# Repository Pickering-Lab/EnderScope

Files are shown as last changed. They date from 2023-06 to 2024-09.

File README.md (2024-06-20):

# EnderScope
The EnderScope is a low-cost scanning microscope, based on the mechanics of the ubiquitous 3D printer, the **Ender 3 Pro**. The hotend of the printer is replaced with an optics module, allowing for the reliable and well calibrated motion system of the 3D printer to be used for automated scanning over a large area.

## Citing
**EnderScope: a low-cost 3D printer-based scanning microscope for microplastic detection**
Niamh Burke, Gesine Müller, Vittorio Saggiomo, Amy Ruth Hassett, Jérôme Mutterer, Patrick Ó Súilleabháin, Daniel Zakharov, Donal Healy, Emmanuel G Reynaud, Mark Pickering
Philosophical Transactions A, 2024, 382 (2274) 20230214, http://doi.org/10.1098/rsta.2023.0214

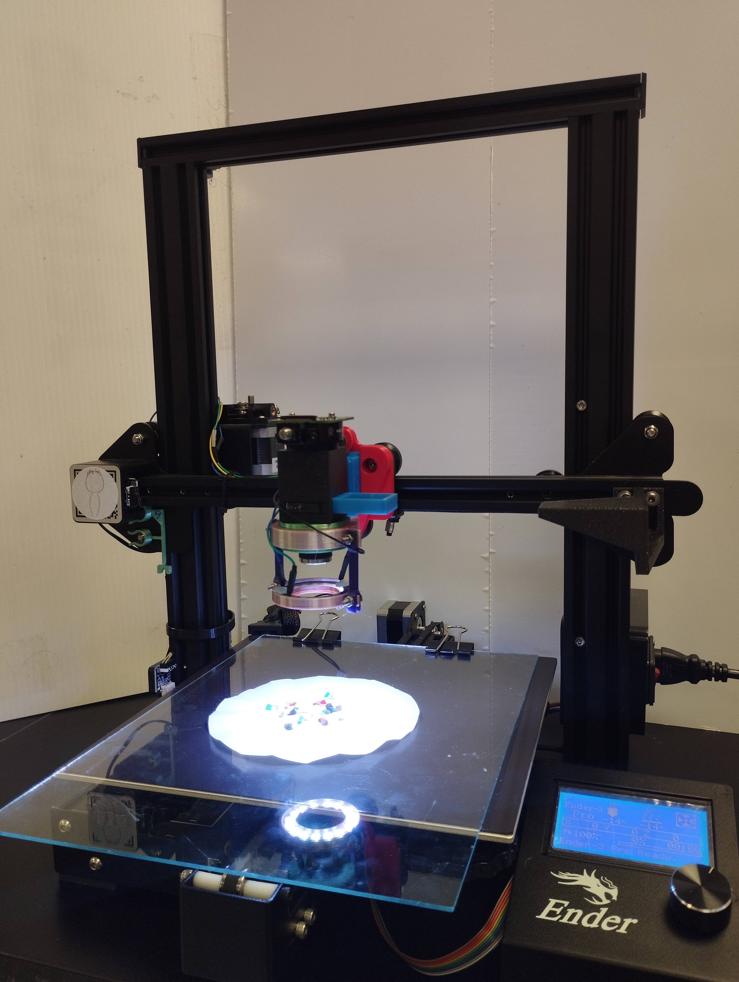
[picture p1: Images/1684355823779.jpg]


## We have reached our funding target on Experiment.com! 🎉
Thanks to your support we have reached our funding target on Experiment.com. Our next step is to get the EnderScope in the hands of Maker Spaces, Community Groups and Libraries accross Ireland. 

Interested in taking part? Contact us on Twitter [@PickeringLab](https://x.com/PickeringLab?s=20) or [@Niamh_deBurca](https://twitter.com/Niamh_deBurca). Watch this space 👀!



# How to Build Your Own EnderScope!
## Hardware
### Bill of Materials
| Part | Qty | Purpose | Source | Price € |
| ----------- | ----------- | ----------- | ----------- | ----------- |
| **Non-printed Parts** |
| Ender 3 Pro | 1 | Motion system of EnderScope | [Link to Ender](https://ie.farnell.com/creality-3d/ender-3-pro/3d-printer-220-x-220-x-250mm-1/dp/2945489) | 224.65 |
| Keyboard & Mouse | 1 | Control of EnderScope | [Link to keyboard and mouse](https://www.amazon.co.uk/Richer-R-Keyboard-Portable-Lightweight-Ultra-Thin-Black/dp/B07CRM63WW/ref=sr_1_5?crid=23O5WNS7BQETO&keywords=usb+keyboard+and+mouse+small&qid=1687527843&sprefix=usb+keyboard+and+mousesmall%2Caps%2C48&sr=8-5) | 15.48 |
| Monitor | 1 | Display for EnderScope | [Link to Monitor](https://www.amazon.co.uk/Dell-Professional-Widescreen-Backlit-Monitor/dp/B00F6390EI/ref=sr_1_5?crid=155O3H11AT8RS&keywords=flat+panel+monitor&qid=1687528400&sprefix=flat+panel+monitor%2Caps%2C56&sr=8-5) | 58.16 |
| HDMI-micro HDMI | 1 | To connect Raspberry Pi to Monitor | [Link to HDMI-microHDMI](https://ie.farnell.com/raspberry-pi/t7733ax/cable-micro-hdmi-hdmi-plug-2m/dp/3107129?gclid=CjwKCAjwhdWkBhBZEiwA1ibLmHy8lcH_6-mT7bqlnekisB4aghKRtLZO5OpQ6GcXcyXmCx-YCe7CPRoCSIsQAvD_BwE&gross_price=true&CMP=KNC-GIE-GEN-SHOPPING-PerformanceMax-TEST-962) | 5.62 |
| 4x RMS Finite Conjugate Objective Lens | 1 |  | [Link to objective lens](https://www.amazon.com/Compound-Microscope-Achromatic-Objectives-Conjugate/dp/B08HW6XMQQ/ref=sr_1_2?crid=2XI5O2ZMWLERR&keywords=rms+finite+conjugate+objective+lens&qid=1674738740&sprefix=rms+finite+conjugate+objective+lens%2Caps%2C127&sr=8-2) | 8.63 |
| Raspberry Pi HQ Camera | 1 | | [Link to HQ Camera](https://ie.farnell.com/raspberry-pi/rpi-hq-camera/rpi-high-quality-camera-12-3-mp/dp/3381605?gclid=CjwKCAjwhdWkBhBZEiwA1ibLmLPRsZ-kTz68qI1Buou0t5rqj3jjkPpFDO3mcRCRjVkKVoDt2jtdiRoC4SUQAvD_BwE&gross_price=true&CMP=KNC-GIE-GEN-SHOPPING-PerformanceMax-No-Impressions) | 56.54 |
| Raspberry Pi 4 Model B | 1 | A low-cost computer used to run the EnderScope | [Link to Raspberry Pi](https://ie.farnell.com/raspberry-pi/rpi4-modbp-4gb/raspberry-pi-4-model-b-4gb/dp/3051887) | 62.20 |
| Pi camera CSI cable (Long ~100cm) | 1 | Connect Raspberry Pi to HQ Camera | [Link to CSI Cable](https://ie.farnell.com/mcm/83-17610/csi-dsi-extension-cable-1-meter/dp/2801336?st=100cm%20csi%20cable) | 6.32 |
| 5V Power Supply USB Type C | 2 | To power Raspberry Pi | [Link to Raspberry Pi power supply](https://ie.rs-online.com/web/p/raspberry-pi-power-supplies/1873424?cm_mmc=IE-PLA-DS3A-_-google-_-CSS_IE_EN_Pmax_Test-_--_-&matchtype=&&s_kwcid=AL!14853!3!!!!x!!&gclid=Cj0KCQjw7uSkBhDGARIsAMCZNJvJgLZ8F8H9JMSdhJQLBEwR4ra1u99iysdaG6aJ2BMPwZ8ZWJeXU8waAowZEALw_wcB&gclsrc=aw.ds) | 9.69 |
| 5V Power Supply USB | 2 | To power Arduino Nano| [Link to 5V power supply](https://www.amazon.co.uk/Charger-Adaptor-Compact-Charging-Samsung/dp/B0BV65Y6B2/ref=sr_1_9?crid=2RVFZQS96QDYE&keywords=5v+wall+charger&qid=1687785970&sprefix=5v+wall+%2Caps%2C58&sr=8-9) | 5.98 |
| Arduino Nano | 1 | To control LED ring | [Link to Arduino](https://store.arduino.cc/products/arduino-nano?queryID=undefined) | 21.60 |
| Push Button | 1 | Turn LED ring on, green or white | [Link to push buttons](https://www.amazon.co.uk/Gikfun-6x6x5mm-Switch-Arduino-EK1019U/dp/B07DQL2GG4/ref=sr_1_1_sspa?crid=17EAN9SJTHE6H&keywords=arduino+push+button&qid=1687538997&sprefix=arduino+push+button%2Caps%2C59&sr=8-1-spons&sp_csd=d2lkZ2V0TmFtZT1zcF9hdGY&psc=1) | 8.09 |
| 220 Ohm Resistor | 1 | For push button | [Link to resistors](https://www.amazon.co.uk/Projects-50EP114220R-220-Resistors-Pack/dp/B0BQ1W9RHK/ref=sr_1_4_sspa?crid=3U55YJR7HT7W&keywords=220+ohm+resistor&qid=1687539054&sprefix=220%2Caps%2C58&sr=8-4-spons&sp_csd=d2lkZ2V0TmFtZT1zcF9hdGY&psc=1) | 6.08 |
| 170 pin breadboard | 1 | For arduino and push button | [Link to breadboard](https://www.amazon.co.uk/SIGNAL-PSG-BB-170W-2BP-Breadboard-Plastic-34-5mm/dp/B01IO3IS12/ref=sr_1_3?crid=2BN9MA6U1KGBD&keywords=170+pin+breadboard&qid=1687539158&sprefix=170+pin+breadboard%2Caps%2C46&sr=8-3) | 3.85 |
| Male to Male Jumper Wires | 7 | For wiring of LED ring and push button | [Link to jumper wires](https://www.amazon.co.uk/2-54mm-Jumper-Wires-Cables-female/dp/B09T3QF6VP/ref=sr_1_48?adgrpid=63845174572&hvadid=291338039024&hvdev=c&hvlocphy=1007850&hvnetw=g&hvqmt=e&hvrand=17576542995084926756&hvtargid=kwd-300565221968&hydadcr=18912_1787284&keywords=male%2Bto%2Bmale%2Bjumper%2Bwires&qid=1687783718&sr=8-48&th=1) | 1.99 |
| USB type A - mini B Cable | 1 | To connect Arduino Nano to 5V power supply | [Link to USB mini cable](https://www.amazon.co.uk/LINDY-36722-Mini-B-Cable-Anthra/dp/B07FN1W4JL/ref=sr_1_3?keywords=mini%2Busb%2Bcable&qid=1687784057&sr=8-3&th=1) | 3.05 |
| USB type A - Micro USB Cable | 1 | To connect Ender to Raspberry Pi| [Link to micro USB cable](https://www.amazon.co.uk/AmazonBasics-Male-Micro-Cable-Black/dp/B07232M876/ref=sr_1_1_ffob_sspa?crid=276BWYDT9STTD&keywords=micro%2Busb%2Bcable&qid=1687784254&s=computers&sprefix=micro%2Busb%2B%2Ccomputers%2C55&sr=1-1-spons&sp_csd=d2lkZ2V0TmFtZT1zcF9hdGY&th=1) | 5.07 |
| Lighting Gels | 1 | Used as Emmission Filter | [Link to lighting gels](https://www.aliexpress.com/item/32695436168.html?pdp_npi=2%40dis%21EUR%21%E2%82%AC%208%2C78%21%E2%82%AC%208%2C78%21%21%21%21%21%4021032fa616703165944567885e866e%2165363130207%21btf&_t=pvid:451ae040-dcc0-4a03-897e-5453e0968200&afTraceInfo=32695436168__pc__pcBridgePPC__xxxxxx__1670316594&spm=a2g0o.ppclist.product.mainProduct) | 7.66 |
| 16 LED Ring | 1 | Illumination Source for Microscope | [Link to LED ring](https://www.amazon.co.uk/Hobby-Components-Ltd-45MM-WS2812B/dp/B01I1D6O48/ref=sr_1_4?keywords=neopixel+16+led+ring&qid=1687539564&sr=8-4) | 9.53 |
| Glass from picture frame, 2mm in thickness, 21x30cm | 1 | Used as a "coverslip" | [Link to picture frame](https://www.ikea.com/ie/en/p/yllevad-frame-black-30429774/?utm_source=google&utm_medium=surfaces&utm_campaign=shopping_feed&utm_content=free_google_shopping_clicks_Decoration&gclid=Cj0KCQjw7uSkBhDGARIsAMCZNJuPV9QcnTO9ueFVAxaAVzIDQurpOPyJlUqf1WcASSWj0xErUw77xK0aAkzMEALw_wcB&gclsrc=aw.ds) | 2.00 |
| Binder Clips | 4 | To hold glass on print bed | [Link to binder clips](https://www.amazon.co.uk/Office-Files-Documents-Metal-Binder/dp/B00W0K3ENS/ref=sr_1_7?keywords=binder+clips&qid=1687796157&sr=8-7) | 2.38 |
| **Screws, Nuts and Tools** |
| M6 12mm Screw | 1 |  |  |  |
| M6 Square Nut | 1 |  |  |  |
| Alan Keys | 1 |  |  |  |
| M3 Screws and Nuts | 4 screws, 4 nuts |  |  |  |
| Scissors | 1 |  |  |  |
| **Total** |  |  |  |  |

### Printed Parts
All 3D-printable files can be found [here](Stls). All files were printed in PLA, with 0.2mm layer height, no supports needed.

## Software
All software for the EnderScope can be found [here](Software).

## Assembly Instructions
Assembly Instructions for the EnderScope can be found [here](AssemblyInstructions).

# Licence and Collaboration

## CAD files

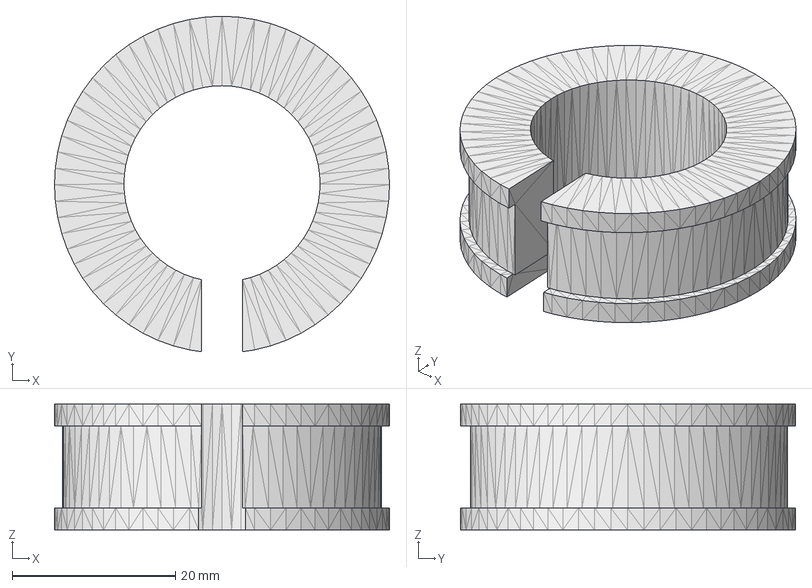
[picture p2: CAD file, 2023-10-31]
STEP/NeopixelClamp_OlympusInsert.step
41.0 x 41.1 x 15.4 mm

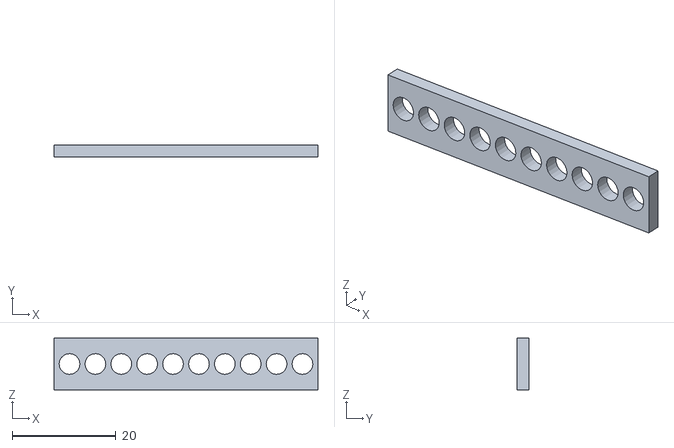
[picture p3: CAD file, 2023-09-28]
Stls/Adjustable LED option/AdjustableArm.stl
51.0 x 2.30 x 10.0

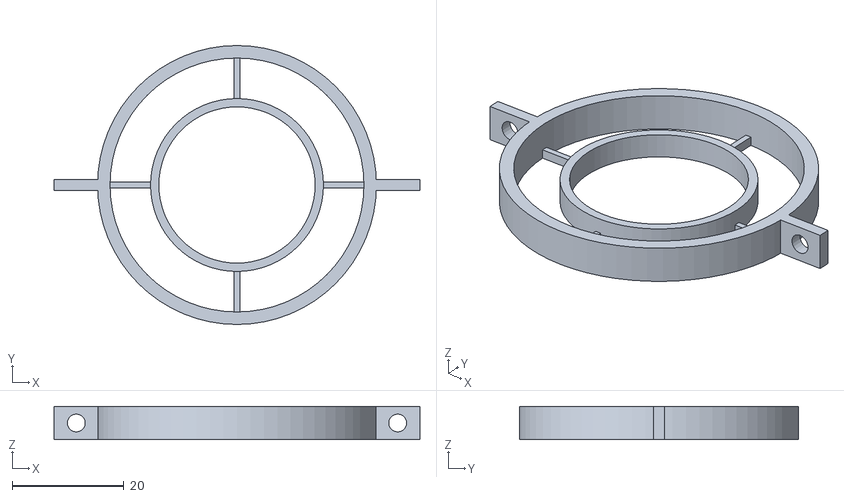
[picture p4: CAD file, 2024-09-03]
Stls/NeopixelMount.stl
65.6 x 50.0 x 6.00

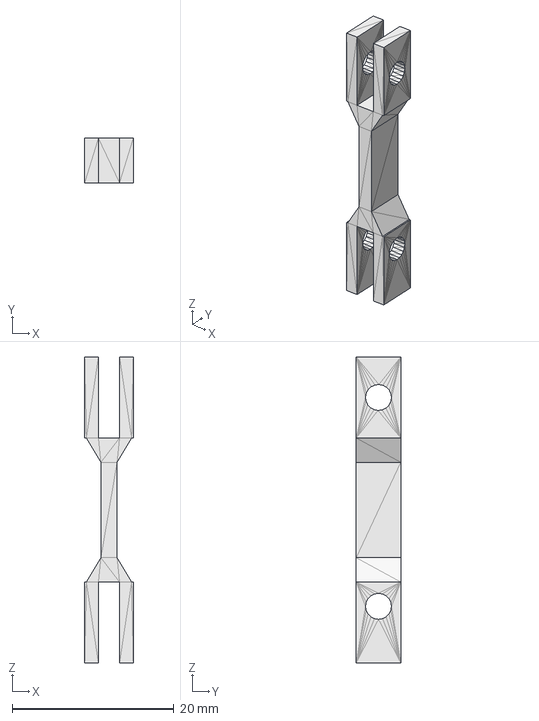
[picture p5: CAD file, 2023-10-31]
STEP/NeopixelConnecter.step
6.00 x 5.50 x 37.8 mm

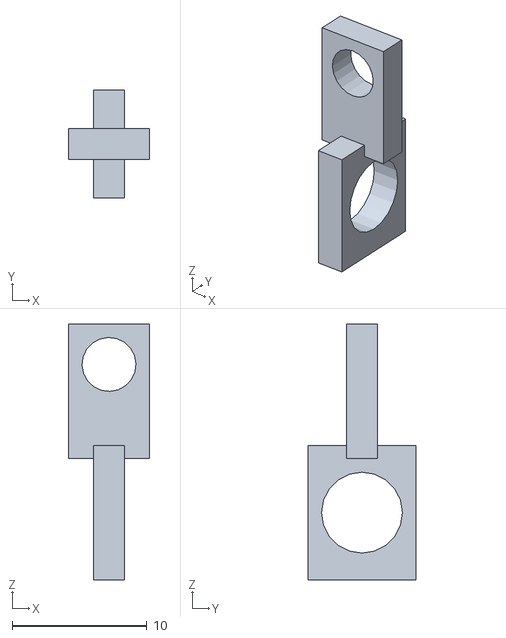
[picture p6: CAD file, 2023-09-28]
Stls/Adjustable LED option/LEDholder.stl
6.00 x 8.00 x 19.0

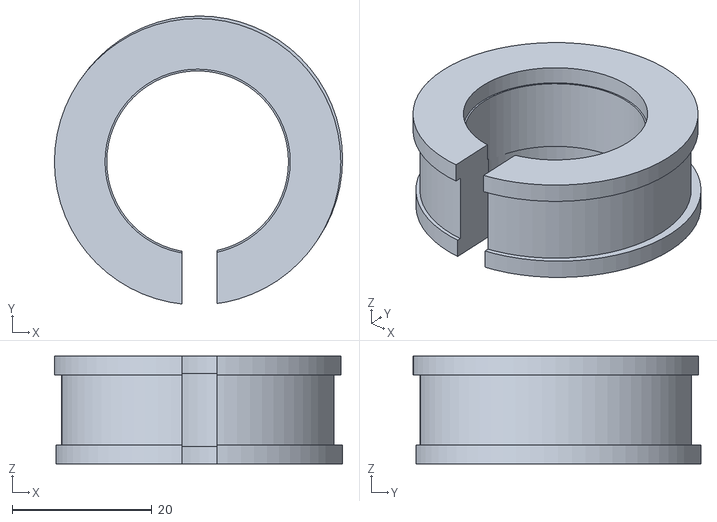
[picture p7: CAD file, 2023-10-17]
Stls/NeopixelClamp_NikonInsert.stl
41.2 x 41.2 x 15.4

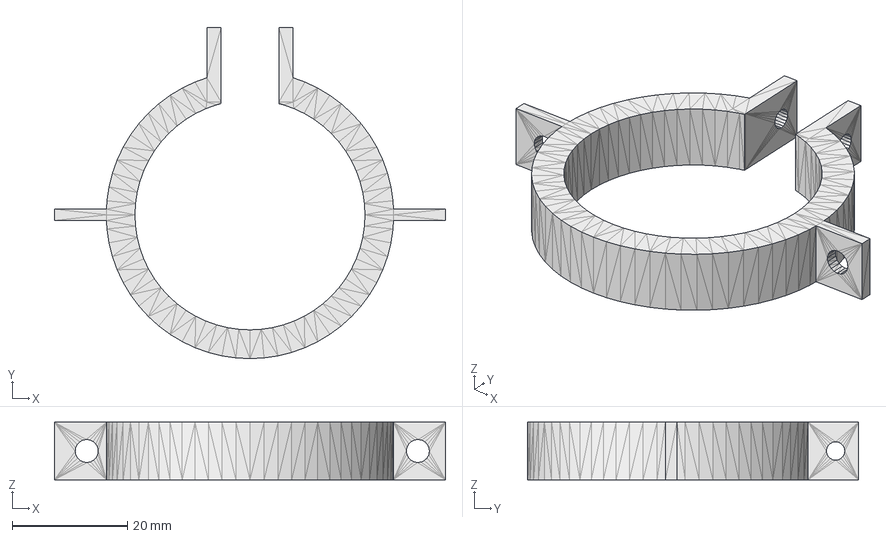
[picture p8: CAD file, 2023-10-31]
STEP/NeopixelClamp.step
68.0 x 57.6 x 10.0 mm

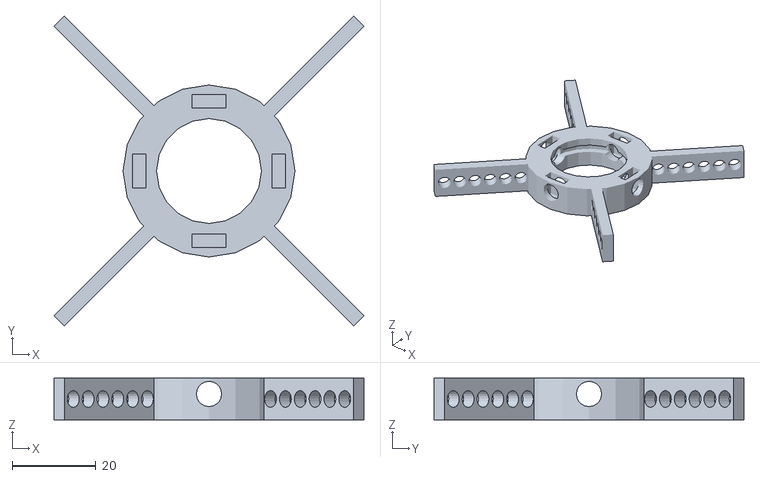
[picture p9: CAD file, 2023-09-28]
Stls/Adjustable LED option/ObjectiveClamp_Oring.stl
73.9 x 73.9 x 10.0

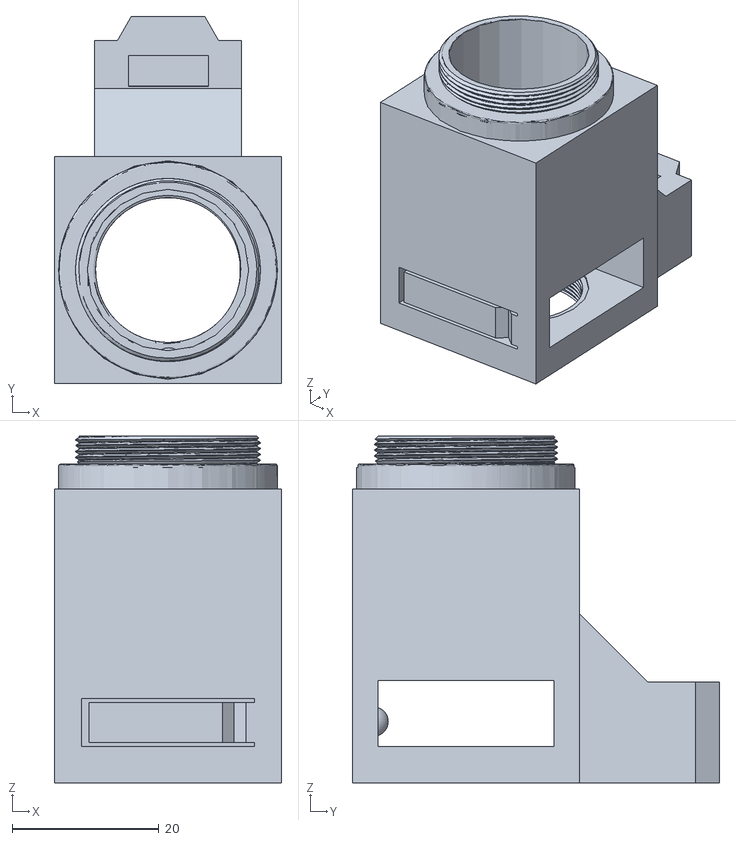
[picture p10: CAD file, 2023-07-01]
Stls/LensTube.stl
31.0 x 50.1 x 47.3

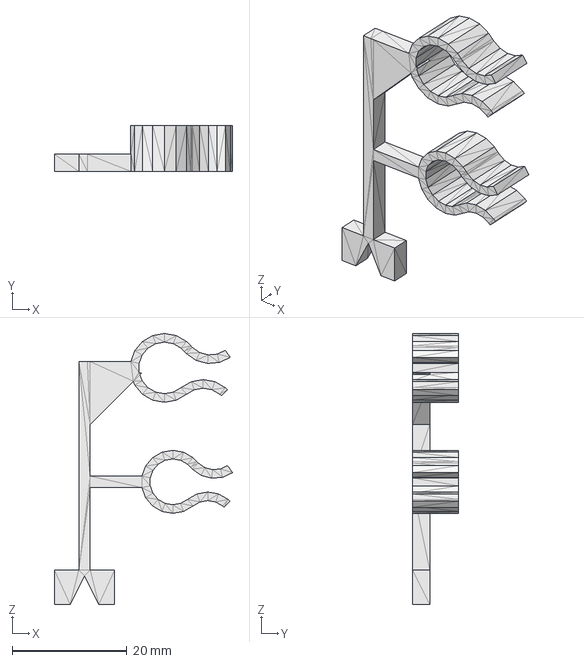
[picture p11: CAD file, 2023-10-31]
STEP/LimitSwitchExtender.step
31.1 x 8.00 x 47.3 mm

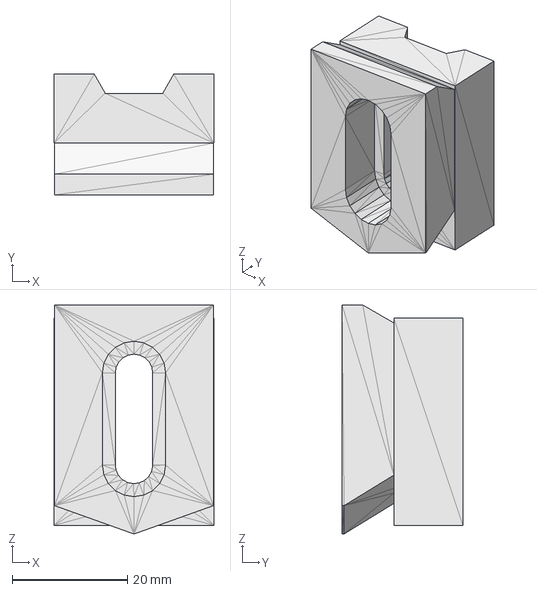
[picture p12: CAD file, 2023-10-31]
STEP/EnderScopeToolHolder.step
27.8 x 21.0 x 39.8 mm

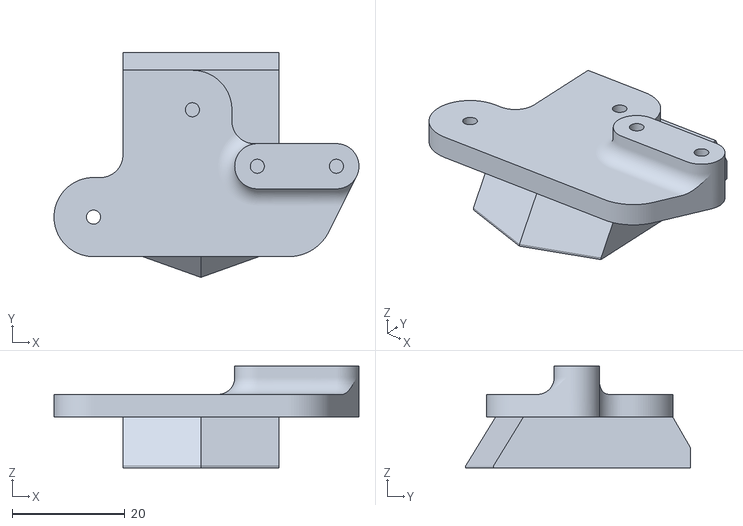
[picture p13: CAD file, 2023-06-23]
Stls/EnderHotendToolHolder.stl
54.0 x 39.8 x 18.0

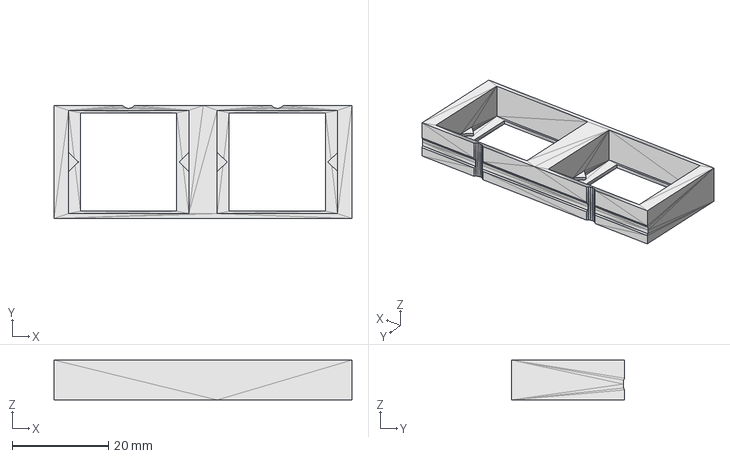
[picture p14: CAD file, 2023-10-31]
STEP/FilterSlider.step
62.0 x 23.5 x 8.30 mm

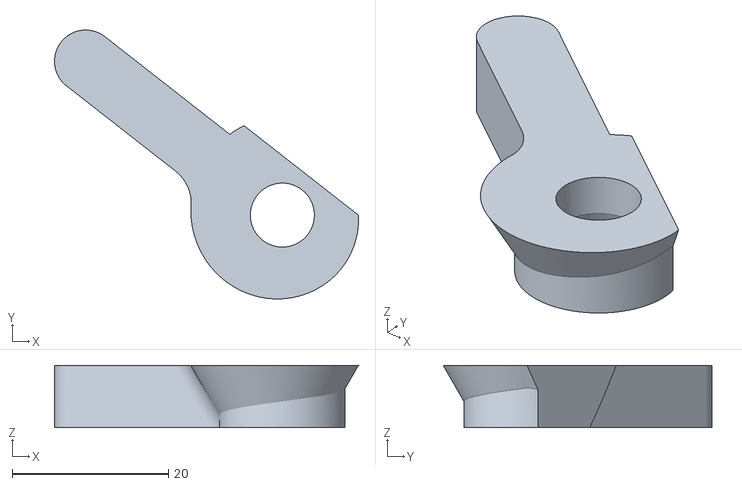
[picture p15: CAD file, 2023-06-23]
Stls/Lever.stl
39.0 x 34.5 x 8.00

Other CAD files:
Stls/NeopixelClamp_GenericInsert.stl
STEP/CableTidy.step
Stls/ToolHolderBase.stl
STEP/ArduinoNanoHolder.step
Stls/ArduinoNanoHolder.stl
Stls/CableTidy.stl
Stls/EnderScopeToolHolder.stl
Stls/FilterSlider.stl
Stls/LimitSwitchExtender.stl
Stls/NeopixelClamp.stl
Stls/NeopixelClamp_OlympusInsert.stl
Stls/NeopixelConnecter.stl

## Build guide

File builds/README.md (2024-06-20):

# A page to gather EnderScope builds and variants
| Printer | Camera | Lens | Illumination | Software | Builder | Application | Comments |
| ----------- | ----------- | ----------- | ----------- | ----------- | ----------- | ----------- | ----------- |
| Ender 3  | Raspberry Pi HQ | 4x | Neopixels with Arduino Nano button | Scripts (link)| Niamh Burke| Detecting microplastics |Original EnderScope |
| Ender 3 S1 | Raspberry Pi HQ | 10x | Neopixels over RPi GPIO | Scripts (meander scan) (link)| Hugo LeGuenno & Jerome Mutterer| Cyanobacteria |Built for MiFoBio2023 |
| Ender 2 Pro | Raspberry Pi Cam V2.1 | - | Neopixels with Arduino Uno firmware for software control (link)| GUI with stage and illumination control and multiposition time-lapse (link)| Jerome Mutterer & Hugo LeGuenno | Seed growth in multiwell plates |Built for MiFoBio2023 |
|- |- |- | Simple Colimation Usson Device (link) |-|Hugo LeGuenno & Yves Usson|Fluorescence| Single high-power RGB LED with easy colimation| 
| - | - | - | Enderlights | [Arduino firmware](enderlights/enderlights.ino)| Jerome Mutterer| Neopixels illumination device that can be driven with a custom set of serial commands |- |

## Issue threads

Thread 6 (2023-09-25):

### ISSUE TITLE
Are there any suggested alternatives for the LED ring / specifications for lighting gels?

### ISSUE THREAD

**Issue by rooksoup** [Pickering-Lab/EnderScope#6]
Hiya,

We have most of the parts to build an EnderScope ourselves and are just missing the cover glass, LED ring and lighting gels. It appears that the LED ring you list is only available through Amazon or that supplier and the lighting gels via AliExpress - are there any suggested equivalents for these that might be more accessible through the annoying constraints of university wholesale suppliers? Has anyone had success with anything a bit different (I imagine it might require some trial and error without the provided Arduino sketch)?

If you have any kind of specs for the LED ring etc. I can have a go at finding something similar and report back :)

**Comment by niamh-deburca** [comment]
Hey,

So for the LED ring, the one we have listed is a cheaper version of the [Adafruit NeoPixel 16 LED ring](https://www.adafruit.com/product/1463). You could swap this out for any LEDs but if you want something that fits in the LED holder it needs to have the following dimensions: 

![image](https://github.com/Pickering-Lab/EnderScope/assets/130670399/b792aff2-63b5-4bb3-94c8-4665c599cea1)

We have also designed an adjustable LED holder. This allows you to hold individual 5mm 2-pin LEDs on adjustable arms and position them around the objective lens. It's a little fiddly to use which is why I didn't have it up on the repository until now but it should be there for you now in case you have some 2-pin LEDs lying around and want to try it.

For the lighting gels we have also tried these [Roscolux filters](https://www.edmundoptics.eu/f/roscolux-color-filter-swatchbook/12186/) which can be bought from Edmund Optics. They work just as well, not expensive and you can get a big swatch book where each filter comes with its own spectral chart. When we are looking to see Nile Red fluorescence, we have found that the Rose pink #342 filter from the swatch book works really well (when you double up two layers of the filter it works especially well).

Hope this helps! Looking forward to seeing another EnderScope in the wild :)

**Comment by rooksoup** [comment]
That's fantastic to know, thank you! Will hopefully report back soon once we get everything together and have a go.

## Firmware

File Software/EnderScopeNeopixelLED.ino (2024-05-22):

#include <Adafruit_NeoPixel.h>

#define PIN            6  // Define the pin to which your NeoPixel strip is connected
#define NUM_LEDS       16 // Define the number of NeoPixels in your strip
#define BUTTON_PIN     2  // Define the pin where the push button is connected

Adafruit_NeoPixel strip = Adafruit_NeoPixel(NUM_LEDS, PIN, NEO_GRB + NEO_KHZ800);

int buttonState = HIGH;
int lastButtonState = HIGH;
unsigned long lastDebounceTime = 0;
unsigned long debounceDelay = 50;
bool ledOn = false;

void setup() {
  strip.begin();
  strip.show(); // Initialize all pixels to 'off'
  pinMode(BUTTON_PIN, INPUT_PULLUP);
}

void loop() {
  int reading = digitalRead(BUTTON_PIN);
  if (reading != lastButtonState) {
    lastDebounceTime = millis();
  }

  if ((millis() - lastDebounceTime) > debounceDelay) {
    if (reading != buttonState) {
      buttonState = reading;

      if (buttonState == LOW) {
        // Button was pressed
        if (ledOn) {
          turnWhite(); // Turn NeoPixels white
          ledOn = false;
        } else {
          turnGreen(); // Turn NeoPixels green
          ledOn = true;
        }
      }
    }
  }

  lastButtonState = reading;
}

void turnGreen() {
  for (int i = 0; i < NUM_LEDS; i++) {
    strip.setPixelColor(i, 0, 255, 0); // Green color
  }
  strip.show();
}

void turnWhite() {
  for (int i = 0; i < NUM_LEDS; i++) {
    strip.setPixelColor(i, 255, 255, 255); // White color
  }
  strip.show();
}

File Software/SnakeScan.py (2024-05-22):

import matplotlib.pyplot as plt
import numpy as np
import serial
from picamera import PiCamera
import time


if __name__ == "__main__":
    folder = "/home/pi/" #Replace this with folder you would like your images saved in
    #Opens serial port
    ser = serial.Serial('/dev/ttyUSB0', baudrate=115200)
    xBase = "G1X"
    yBase = "Y"
    endTerm = "\n"
    speed = 18000   #max_speed
##     Uncoment to home printer at beginning of script - ***WARNING*** You must make sure objective lens will not crash in to bed before homing. Attach limit switch extender or remove optics module during homing.
#     home = "G28" + "F" + str(speed) + "\n"
#     home = home.encode('utf-8')
#     ser.write(home)
    x_mid = 0
    y_mid = 0
    startPos = xBase + str(x_mid) + yBase + str(y_mid) + "F" + str(speed) + endTerm
    startPos = startPos.encode('utf-8')
    ser.write(startPos) # go to half max
    # open camera (image acquisition)
    camera = PiCamera()

def snake(x_win, y_win, x_step, y_step):
    a = []  # List of X positions
    b = []  # List of Y positions
    x = 0
    y = 0  # Start point at the bottom left corner
    
    for j in range (y_win - 1):
    
        if j == 0 :
            
            for i in range(x_win): #increment x step
                
                if i % x_win != 0:
                    dx = x_step
                    dy = 0
                    
                elif i % x_win == 0:
                    dx = 0
                    dy = 0
                    
                x = x + dx
                y = y + dy
                
                a.append(x) #take list a and stick x into it, so 0 is first number in list
                b.append(y) #take list b and stick y into it, so 0 is first number in list 
            
        
        if j % 2 != 0:
            
            for i in range(x_win):
                
                if i % x_win != 0:
                    dx = x_step
                    dy = 0
                    
                elif i % x_win == 0:
                    dx = 0
                    dy = y_step
                    
                x = x + dx
                y = y + dy
                
                a.append(x) 
                b.append(y)      
                        
        elif j % 2 ==0:
            
            for i in range(x_win):
            
                if i % x_win != 0:
                    dx = -x_step
                    dy = 0
                    
                elif i % x_win == 0:
                    dx = 0
                    dy = y_step
                
                x = x + dx
                y = y + dy
                
                # Round the x-value to 2 decimal places
                x = round(x, 2)
                
                a.append(x) 
                b.append(y)
                
    x_vals = np.array(a)
    y_vals = np.array(b)
    print (x_vals)
    print (y_vals)
    return a, b

x_win = 3  # Number of steps in the x direction
y_win = 3 # Number of steps in the y direction
x_step = 5  # Step size in the x direction
y_step = 5  # Step size in the y direction
x_mm = x_win*x_step # to calculate area scan will cover in mm
y_mm = y_win*y_step


x, y = snake(x_win, y_win, x_step, y_step)


tune = "M300 S440 P200" + endTerm 
ser.write(tune.encode('utf-8')) # play tune to signal start of scan
pause = "M18" + endTerm # disable stepper - allows user to position optics module in bottom left corner of sample
ser.write(pause.encode('utf-8'))
camera.start_preview(fullscreen=False, window=(100, 100, 640, 480))
print('Steppers have been disabled')
print('Ensure sample is in focus. Then move optics module to bottom left corner of sample')
input("Press the Enter key to proceed")
camera.stop_preview()
resume = "M108" + endTerm
ser.write(resume.encode('utf-8'))

print('This is the path of the snake scan. Close graph to proceed.')
plt.plot(x, y, marker = 'x') # plots path of scan
plt.xlabel('X')
plt.ylabel('Y')
plt.title('Snake Scan')
plt.grid(True)
plt.show()


print(f"This will now start a snake scan, scanning over an area {x_mm} x {y_mm} mm starting from the bottom left corner of the sample, going right and up")
input("Press the Enter key to proceed")
resume = "M108" + endTerm
ser.write(resume.encode('utf-8'))

camera.start_preview(resolution=(640, 480))
for i, (x_val, y_val) in enumerate(zip(x, y), start=1):
        # Move the printer here (adjust the timing as needed)
    xPos = x_mid + x_val
    yPos = y_mid + y_val
    Mot = xBase + str(xPos) + yBase + str(yPos) + "F" + str(speed) + endTerm
    Mot = Mot.encode('utf-8')
    ser.write(Mot)
    time.sleep(1)
    # Use string formatting to create the file name with leading zeros
    num_digits = len(str(len(x)))  # Determine the number of digits needed
    file_name = f"{folder}_{i:0{num_digits}d}.bmp"
    camera.exposure_mode = 'off'
    camera.awb_mode = 'off'
    camera.resolution = (1014, 760)
    # Configure white balance and exposure settings for each image capture
    camera.awb_gains = (1, 1)  # R and B gains, both set to 1.0 for neutral white balance
    camera.shutter_speed = 8000 # exposure setting - adjust as needed particularly for fluorescence imaging
    
    # Capture the image with the constructed file name
    camera.capture(file_name)
    time.sleep(1)
# Close the camera preview when the scan is finished
camera.stop_preview()

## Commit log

2023-06-23 Add files via upload
    v1 Assembly Images
2023-06-23 Add files via upload
    v1 stls
    [Copy of Adjustable Neopixel Clamp v5.stl, Copy of Adjustable illumination clamp 2.3 Amazon insert v3.stl, Copy of EnderHotendToolHolder.stl, Copy of FluoEnderT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]
2023-06-26 easier to print without support
    [Long RMS threads_lenstube 2.3_edits (2).stl]
2023-06-26 v1.2 files (renamed)
    renamed and cable tidy and arduino holder added
    [ArduinoNanoHolder.stl, Cable Tidy.stl, EnderHotendToolHolder.stl, EnderScopeToolHolder.stl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]
2023-06-29 Replaced LimitSwitchExtenderv9 with v10 (shorter)
    [LimitSwitchExtender.stl]
2023-09-28 Add files via upload
    Uploaded stl files for adjustable LED mount
    [AdjustableArm.stl, LEDholder.stl, ObjectiveClamp_Oring.stl]
2023-10-17 Add files via upload
    Inserts for Nikon CF N Plan Achromat 4X/0.13 objective lens and Olympus Plan Achromatic 4x
    [NeopixelClamp_NikonInsert.stl, NeopixelClamp_OlympusInsert.stl]
2023-10-26 Add files via upload
    Renamed without space in name
    [CableTidy.stl]
2024-06-23 Create How to Collect and Process a Microplastics Sample
2024-06-25 Add files via upload
    Slight changes to assembly instructions for ECP
2024-06-25 Create How to Collect and Process a Microplastics Sample.md
2024-06-25 V2 Assembly Instructions
    Point out where motherboard is and correct M4 to M2.5 screws
2024-08-20 Shorter wings (corrected file)
    [NeopixelMount.stl]
2024-09-03 Corrected file (shorter wings, one piece)
    [NeopixelMount.stl]
2024-12-03 Update enderlights.ino
    add modes and parameters commands for sectors or single LED illuminations
